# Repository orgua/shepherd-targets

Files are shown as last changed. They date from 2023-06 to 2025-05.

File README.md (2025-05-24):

# Target Boards & Firmware





**Main Documentation**: <https://nes-lab.github.io/shepherd>

**Source Code**: <https://github.com/nes-lab/shepherd-targets>

**Main Project**: <https://github.com/nes-lab/shepherd>

---

The repository contains a collection of target-hardware and mcu-firmwares used by the shepherd-testbed.
In the past shepherd had a nRF52-only target but can now leverage an additional FRAM, as demonstrated successfully by the
[Riotee-Platform](https://www.riotee.nessie-circuits.de).

**NOTE**: The shepherd testbed has a second target-port (unused) and is looking for ideas.
Just contact us if you got ideas.

## nRF52 with MSP430FR as FRAM

Hardware v1.3+ uses

- nRF52840
- MSP430FR5994 (TI)
- RTC AB1805

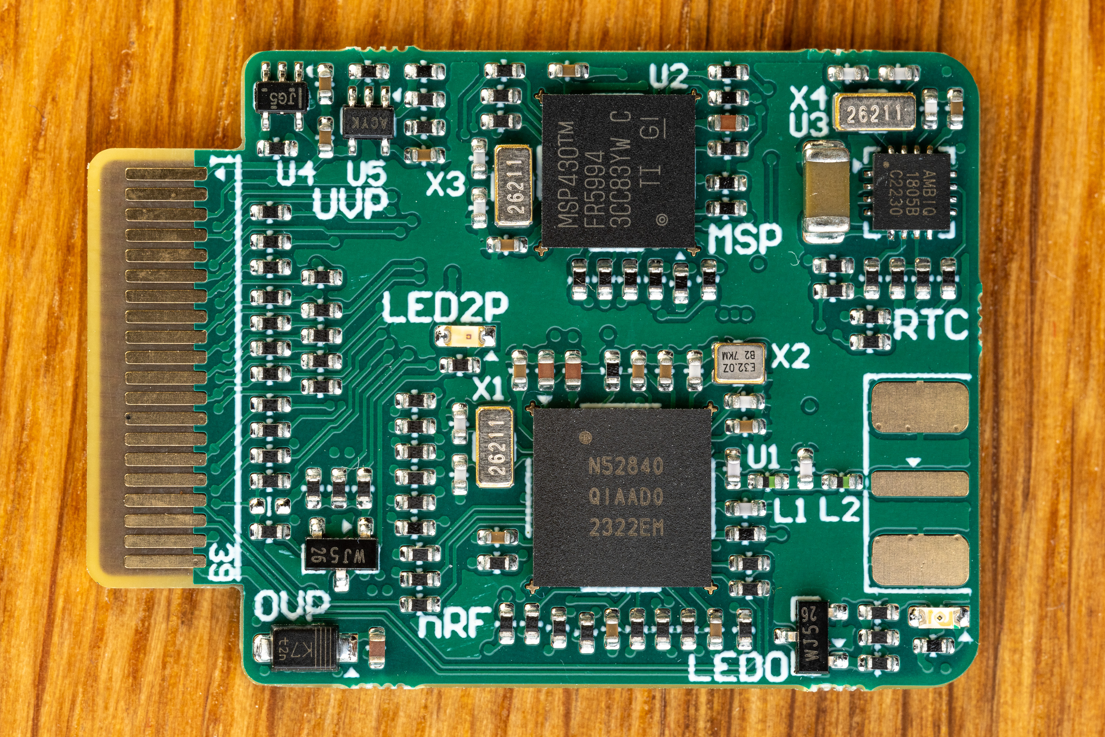
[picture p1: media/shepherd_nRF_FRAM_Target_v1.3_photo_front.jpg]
Target_nRF_MSP430


BOM, gerber-files and schematics are available in the [PCB-Directory](https://github.com/nes-lab/shepherd-targets/tree/main/hardware).
This folder also contains a guide for testing new target-PCBs.

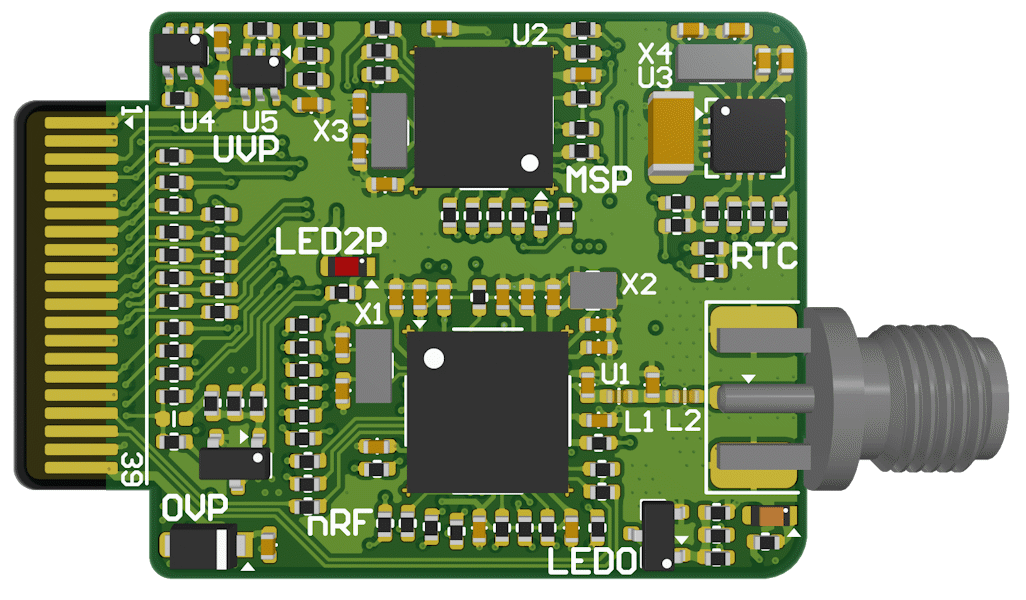
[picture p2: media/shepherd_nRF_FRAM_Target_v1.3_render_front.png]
Target_nRF_MSP430_render


### Features

- freedom to use both MCUs as needed (just as radio or FRAM) or disable when not needed (deep sleep)
- over-voltage protection for V_LV (max 3.9V)
- under-voltage protection with hysteresis for nRF
- one debug LEDs with separate supply for minimal impact on pwr-budget
- one self-powered LED to "burn" energy
- io pins not interfering with RF (nRF PS v1.6 page 578)
- LEDs / UART similar to [Riotee](https://www.riotee.nessie-circuits.de/)
- nRF uses low voltage mode (PSv1.1 page 61)
- 16x GPIO shared to host, current-limited with 240R star-configuration (every participant has that resistor on its port to also keep data rates >10 MHz)
- high & low power-good-signal (similar to riotee)
- SMA-port for external antenna
- 3rd possible way for reset (external), beside jtag and pwr-cycle

### nRF52-Firmwares

- [nrf52_demo_rf](https://github.com/nes-lab/shepherd-targets/tree/main/firmware/nrf52_demo_rf): demo implementation for a simple node that sends BLE packets when energy budget allows it
- [nrf52_testable](https://github.com/nes-lab/shepherd-targets/tree/main/firmware/nrf52_testable): watches all gpio and reports with UART messages (verification after assembly)
  - ensures that pcb is assembled OK and both MCUs are programmable and show basic functions
  - what is not tested: watchdog, FRAM, RF-Frontend (-> use rf-demo or rf-survey), sleep power consumption
- [nrf52_rf_test](https://github.com/nes-lab/shepherd-targets/tree/main/firmware/nrf52_rf_test): sends out 1 BLE-Packet per second (verify with an app like `RaMBLE`)
- [nrf52_rf_survey](https://github.com/nes-lab/shepherd-targets/tree/main/firmware/nrf52_rf_survey): Link Matrix Generator - TX-Unit - sends packet with every possible P_TX, loops until stopped
- [nrf52_deep_sleep](https://github.com/nes-lab/shepherd-targets/tree/main/firmware/nrf52_deep_sleep): practically turned off MCU with the lowest possible consumption

- TODO: nrf52_spi_radio - default implementation to use nRF as a radio frontend

### MSP430FR-Firmwares

- [msp430_deep_sleep](https://github.com/nes-lab/shepherd-targets/tree/main/firmware/msp430_deep_sleep): practically turned off MCU with the lowest possible consumption
- [msp430_spi_fram](https://github.com/nes-lab/shepherd-targets/tree/main/firmware/msp430_spi_fram): [riotee](https://github.com/NessieCircuits/Riotee_MSP430Fram) implementation to use MSP as a flash storage
- [msp430_testable](https://github.com/nes-lab/shepherd-targets/tree/main/firmware/msp430_testable): switches on all shared gpio one by one (verification after assembly)

## Getting started

Step by step description for installing all prerequisites to compile the firmware.

### nRF52

- Make sure you have the [GNU Arm Embedded Toolchain](https://developer.arm.com/tools-and-software/open-source-software/developer-tools/gnu-toolchain/gnu-rm/downloads) installed
- If `arm-none-eabi-gcc` is not in your path, set the environment variable `GNU_INSTALL_ROOT` accordingly, e.g.: `export GNU_INSTALL_ROOT=/opt/toolchain/` (note the trailing foreslash)
- Download the nRF5 SDK from [here.](https://www.nordicsemi.com/Software-and-tools/Software/nRF5-SDK/Download) (You don't need a SoftDevice) and extract it
- Set the environment variables `SDK_ROOT` to the corresponding absolute path, e.g.: `export SDK_ROOT=/home/user/nRF5_SDK_17.0.2_d674dde/`
- run `make`

Refer to [the GitHub workflow](https://github.com/nes-lab/shepherd-targets/tree/main/.github/workflows/build_nrf.yaml) for how to install the toolchain and build the project.

### MSP430

To build the code, you'll need the gcc toolchain for the MSP430 microcontroller series. Refer to [the GitHub workflow](https://github.com/nes-lab/shepherd-targets/tree/main/.github/workflows/build_msp.yaml) for how to install the toolchain and build the project.

### Controlling the Node-ID

When an `elf`-firmware contains a ``SHEPHERD_NODE_ID``, the variable will be patched with the actual target-ID before running the experiment. See the proposed [c-file](https://github.com/nes-lab/shepherd-targets/tree/main/firmware/nrf52_demo_rf/src/shepherd_node_id.c) for more information.

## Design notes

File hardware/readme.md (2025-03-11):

# PCBs and other hardware

This directory contains all files to manufacture hardware:

- schematic
- PCB-renderings (end of schematic pdfs)
- gerber for pcb manufacturing
- BOM to order parts
- pick and place and assembly drawings for PCB assembly

## nRF52 & MSP430 FRAM Target

- V1.0 was the initial target used by the testbed
- ~~V1.1 was designed, but is not yet manufactured~~
- ~~V1.2 was designed and tested - discarded because of manufacturing problems~~
- V1.3 is being deployed ATM
- V1.3e will accompany the base-version and will hopefully reduce failure-rate of msp430

## Adapters

- debug-board for target v1.3 that can sit between cape and target and breaks out all GPIO to 0.1" header
- converter for cape v2.4 header to target v1.3 edge-connector

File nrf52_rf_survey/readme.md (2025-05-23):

# nRF using TrafficBench to survey the rf-conditions for the testbed

Trafficbench is configured to let each node send a packet. The other nodes listen automatically and try to capture the packet and also record the P_Rx.

Current configuration

- loop - one node after the other talks - the others listen
- each node sends ~ 34 bytes via 1 MBit Bluetooth (~300 us airtime), PTx = 0 dBm
- the other nodes listen and capture for 5 ms (+ 500 us pre- & post-delay)
- sleep 1 s before next node begins

## Installation

- adapt schedule with the [schedule-builder-script](./schedule_builder/build.py)
- compiling: follow the [readme](./trafficbench/README.md) of trafficbench
  - newest studio version (tested with v7.30) is fine
  - extra package needed (and restart studio after install) - should be automatic: CMSIS 5 5 CMSIS-CORE Support Package

## Usage of ELF

- patch SHEPHERD_NODE_ID in elf-file for each node (see [example python script](./_build/update_and_patch.py))
- run on testbed
- postprocessing, TODO
- NOTE: first loop-cycle should be discarded

## Changes compared to vanilla trafficbench

- change testbed: flocklab -> shepherd
- correct spelling
- fix formatting
- fix for sensitivity to include-order: added #include "traffic_bench.h" in cbor.h
- removed node-id-magic in main.c (line 154:217)
- transformed py-scripts to be more accessible

specially for shepherd

- reduced uart-speed to 115_200 for now (in config.h)
- disable flow control (readme warns about it) to just stream uart (`mode=0` in config.h)
- disable button press to start (section removed in main.c)
- deactivate DEBUG_GPIO in `radio.c`
- current GPI modifications
  - reformatted with projects clang-format
  - use `GPI_ARCH_BOARD_TUDNES_SHEPHERD_NRF52840FRAM_V13` as `GPI_ARCH_PLATFORM` in `trafficbench/config.h`
  - added `#include "gpi/arm/nordic/nrf528xx/platform_internal.h"` in `trafficbench/target/nrf52840/radio_queues_custom.h` to add back macros for trafficbench
  - added `#define LED_SYNC GPI_LED_0` for our target `#elif GPI_ARCH_IS_BOARD(TUDNES_SHEPHERD_NRF52840FRAM_V13)` in `trafficbench/scheduler.c`

## Usage on the testbed

on server - prereq:

```shell
cd ~
git clone https://github.com/nes-lab/shepherd-tools
cd shepherd-tools/extr

python3 gen_energy_envs.py
python3 gen_firmwares.py
python3 gen_rf_survey.py
# current firmware is now in /var/shepherd/content/fw/, accessible by all observers
# task is also accessible for all observers, but in our case we send it out via herd-tool
```

for the actual run:
```Shell
shepherd-herd -v run -a /var/shepherd/content/task/nes_lab/tasks_rf_survey.yaml
# this takes ~ 8min and will exit after. Then we collect the data
scp
```

scp /var/shepherd/recordings/

## TODO:

- vary send-power (?)
- look for other IO used by TB
  - gpi_button_read() in main.c
  - gpi_led_toggle() in main.c
  - gpi_led_on() & gpi_led_off() in scheduler.c
  - LED_SYNC, GPI_LED_2
  - GPI_BUTTON_SIG1, GPI_BUTTON_1
- py:
  - filter_log.py and more
  - make code usable by other py-code
  - modularize + make testable
- speed up loop
  - 1 ms tx-delay
  - 3 ms tx-timeout
  - 15 - 50 ms sleep
  - factor in TRX_PRE_DELAY and _POST_DELAY
- packet-content: all random data might improve prx-consistency

## Source

https://gitlab.com/nes-lab/trafficbench

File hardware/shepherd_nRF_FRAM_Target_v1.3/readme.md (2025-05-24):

# nRF52 & MSP430 FRAM Target V1.3

Shared pins between MCUs and Observers with **Cape V2.5 (currently evaluated)**.
**The testbed still uses Cape v2.4 as of 2025-04. See 2nd table below for that mapping.**

| SHP-V26  | Dir   | Riotee     | nRF52  | msp430  | Description                 |
|----------|-------|------------|--------|---------|-----------------------------|
| GPIO0    | <-A-> | GPIO.0     | P0.21  | P2.6    | UART Target-RX, msp.A1.CiPo |
| GPIO1    | <--   | GPIO.1     | P0.08  | P2.5    | UART Target-TX, msp.A1.CoPi |
| GPIO2    | <-B-> | GPIO.2     | P0.04  | P2.3    | msp.A1.PSel                 |
| GPIO3    | <-B-> | GPIO.3     | P0.05  | P2.4    | msp.A1.CLK                  |
| GPIO4    | <-C-> | GPIO.4     | P1.09  | P4.6    |                             |
| GPIO5    | <-C-> | GPIO.5     | P0.26  | P3.6    |                             |
| GPIO6    | <-C-> | GPIO.6     | P1.03  | PJ.6    |                             |
| GPIO7    | <-C-> | GPIO.7     | P0.11  | P5.3    | msp.B1.PSel                 |
| GPIO8    | <--   | GPIO.8     | P0.13  | P5.2    | msp.B1.CLK                  |
| GPIO9    | <--   | GPIO.9     | P0.16  | P5.1    | msp.B1.CiPo                 |
| GPIO10   | <--   | -          | P0.12  | P5.0    | msp.B1.CoPi, SDA            |
| GPIO11   | <--   | -          | P0.10  | P6.0    | msp.A3.CoPi, TXD            |
| (GPIO12) | <--   | -          | P0.19  | P6.1    | msp.A3.CiPo, RXD            |
| (GPIO13) | <--   | -          | P0.20  | P6.3    | msp.A3.STE                  |
| (GPIO14) | <--   | -          | P0.24  | P6.6    | msp.A3.CLK                  |
| (GPIO15) | <--   | -          | P0.27  | P6.7    | msp.A3.STE                  |
| PwrGoodL | -->   | PG_L       | P0.23  | P5.4    |                             |
| PwrGoodH | -->   | PG_H       | P0.07  | P5.5    |                             |
| prog11   | -->   | SWD.CLK    | swdclk | -       |                             |
| prog12   | <-D-> | SWD.IO     | swdio  | -       |                             |
| prog21   | -->   | SBW.CLK    | -      | sbwtck  |                             |
| prog22   | <-E-> | SBW.IO     | -      | sbwtdio |                             |
|          | -     | LED.0      | P1.13  | P5.7    |                             |
|          | -     | LED.2P     | P0.03  | PJ.0    |                             |
|          | -     | I2C.SCL    | P1.08  | P6.5    |                             |
|          | -     | I2C.SDA    | P0.06  | P6.4    |                             |
|          | -     | RTC.INT    | P0.30  | P7.3    | shared, no fct for shp      |
|          | -     | MAX.INT    | P0.30  | PJ.1    | shared, no fct for shp      |
|          | -     | C2C.CLK    | P0.18  | P1.5    | msp.A0.CLK                  |
|          | -     | C2C.CoPi   | P0.17  | P2.0    | msp.A0.CoPi                 |
|          | -     | C2C.CiPo   | P0.14  | P2.1    | msp.A0.CiPo                 |
|          | -     | C2C.PSel   | P0.22  | P1.4    | msp.A0.PSel                 |
|          |       | C2C.GPIO   | P0.15  | PJ.2    |                             |
|          |       | THRCTRL.H0 | P0.09  | P1.3    | shared, no fct for shp      |
|          |       | THRCTRL.H1 | P1.02  | P3.3    | shared, no fct for shp      |
|          |       | THRCTRL.L0 | P1.07  | P6.2    | shared, no fct for shp      |
|          |       | THRCTRL.L1 | P1.04  | P7.0    | shared, no fct for shp      |
|          |       | VCAP.Sense | P0.29  | P7.5    | VTarget                     |

**Note**:

- A, B, C in DIR-Column refer to switch-groups. 1, 2 and/or 4 bits can be reversed to talk to the target.
- D, E are switch-groups needed for programming
- Shepherds GPIO12 to GPIO15 are not recordable by the testbed as pins on the SBC are all used up

## Connections to Cape V2.4 via Adapter

The 40-pin Edge-Connector of Target V1.3 has an adapter to interface the 2x9 Header of Cape V2.4. This keeps connections compatible to Target V1.0.

| SHP-V24 | Dir   | Riotee   | nRF52  | msp430  | Description                 |
|---------|-------|----------|--------|---------|-----------------------------|
| GPIO0   | <-A-> | GPIO.7   | P0.11  | P5.3    | msp.B1.PSel                 |
| GPIO1   | <-A-> | GPIO.8   | P0.13  | P5.2    | msp.B1.CLK                  |
| GPIO2   | <-A-> | GPIO.2   | P0.04  | P2.3    | msp.A1.PSel                 |
| GPIO3   | <-A-> | GPIO.3   | P0.05  | P2.4    | msp.A1.CLK                  |
| GPIO4   | <--   | GPIO.4   | P1.09  | P4.6    |                             |
| GPIO5   | <--   | GPIO.5   | P0.26  | P3.6    |                             |
| GPIO6   | <--   | GPIO.6   | P1.03  | PJ.6    |                             |
| GPIO7   | <--   | GPIO.1   | P0.08  | P2.5    | UART Target-TX, msp.A1.CoPi |
| GPIO8   | <-B-> | GPIO.0   | P0.21  | P2.6    | UART Target-RX, msp.A1.CiPo |
| BATOK   | -->   | PG_H     | P0.07  | P5.5    |                             |
| prog11  | -->   | SWD.CLK  | swdclk | -       |                             |
| prog12  | <-C-> | SWD.IO   | swdio  | -       |                             |
| prog21  | -->   | SBW.CLK  | -      | sbwtck  |                             |
| prog22  | <-D-> | SBW.IO   | -      | sbwtdio |                             |

**Note**:
- A, B, C, D in DIR-Column refer to switch-groups
- Shepherds GPIO8 (target-rx) will be re-assigned to PwrGoodL (BATOK is PwrGoodH)
  - TODO: Resistor-Switch on adapter available, but software not ready yet

## Features

- similarity to Riotee
- MCU 1 - nRF52840
- MCU 2 - msp430FR5994
- low power RTC & Watchdog
- one led to burn energy fast
- SMA port to connect external antenna
  - balun is optimized for higher transmit power (>= 5 dBm, ref circuit 7 in PS v1.8)
- MCUs share SPI-Connection + some additional pins
- edge-connector routes out
  - programming pins (SWD & SBW)
  - power-good signals
  - 16x shared GPIO
- all shared GPIO is current limited to prevent damages to the hardware
  - limit to 8-10 mA @ 4V with 470 R or (2x) 220 R on each IC entry
- IO-Pins not interfering with RF (nRF PS v1.6 page 578)
- clock-crystals have high precision, 5 ppm, with matched impedance
- protection for over- & under-voltage, see sub-chapters below

### Over-Voltage-Protection

The target voltage coming from the shepherd-cape can reach up to 5 V.
The MCUs on the target board can't handle that voltage, so the ICs have to be protected.

Abs Max Ratings:

- 3.9 V nRF52
- 3.8 V RTC AB1805
- 4.1 V MSP430

A fitting shottky diode is used to burn energy above 3.7V.

One PMEG10010ELR Diode is between V_target and 3V3:
+ 0.0 V -> 6 pA (noise)
+ 0.1 V -> 47 nA
+ 0.2 V -> 2.3 uA
+ 0.3 V -> 120 uA
+ 0.4 V -> 4.83 mA

### Under-Voltage-Protection

- the nRF consumes ~.5mA below 1.7V, even in deep-sleep
- consumption drops when going above 1.69 V
- consumption rises when going below 1.58 V
- tested 13 nodes range from
   - ON = 1.63 to 1.69 V
   - OFF = 1.58 to 1.60 V

Solution

- analog switch controlled by comparator with small hysteresis
- VON = 1.729 V, VOFF = 1.652 V according to formular in datasheet (values are wrong?)
- VON = 1.797 V, VOFF = 1.642 V when solving the network with traditional methods
- VON = 1.802 V, VOFF = 1.641 V from actual measurements

Possible Caveats

- hysteresis is currently only 150 mV and unstable behavior must be avoided
- charging the decoupling caps (2.6 uF) of the MCUs leads to voltage drop
  - 10 uF storage, 2.6 uF decoupling -> 230 mV drop (trouble)
  - 47 uF storage, 2.6 uF decoupling -> 48 mV drop
  - 100 uF storage, 2.6 uF decoupling -> 22 mV drop
- turning on the switch shows current spike of ~ 4 mA for < 50 us for target v1.0 with 1.6 uF decoupling
  - 10 uF storage, 5 mA draw -> 200 us for 100 mV drop
  - 10 uF storage, 1 mA draw -> 1000 us for 100 mV drop
  - 47 uF storage, 5 mA draw -> 940 us for 100 mV drop
  - 100 uF storage, 5 mA draw -> 2000 us for 100 mV drop

Calculating the charging drop for the decoupling caps with `maxima`:

```maxima
C_store: 10e-6;
C_out: 2.6e-6;
V_set: 1.7;
dVc: V_set * (sqrt(1 - C_out / C_store) - 1);
```

Calculating the allowed time for high current during switching on:

```maxima
V_set: 1.7;
C_store: 10e-6;
I_out: 5e-3;
dV: 100e-3;
t: dV * C_store / I_out;
```

See `.wxmx`-maxima-file for more details.

## Difference to Riotee

- nRF52840 instead of Riotees -833
  - main makefile specifies `NRF_DEV_NUM`
- msp430FR5994 has more storage (256 KB)
  - Size of FRAM auto-adjust? -> main makefile `RIOTEE_RAM_RETAINED_SIZE`, `RIOTEE_STACK_SIZE`
- extra LED.0
- 16x GPIO instead of 10x
- no power-converters, but over-voltage-protection and under-volt-switch for nRF

## Bugs of prior Version & Proposed Fixes / Improvements

- nRF - remove resist of alignment crosses
- less paste on thermal pad of nRF? Thermal paste is OK
  - solder on thermal is 9 * 1.1² = 8.6 mm² (round) -> 38 %
  - info: nRF-IC thermal pad ~4.75², 22.6 m² (IC and footprint match)
- make ABx Thermal pad bigger
  - info: ABx-IC thermal pad is ~ (1.8 mm)²
  - datasheet says D2xE2 is 1.65 - 1.75 - 1.85 -> area: 2.6 - 3.1 - 3.4 mm²
  - footprint was (1.13mm)² with 50% paste reduction (1.27 / 0.65 mm²)
  - now it is 1.5² with 65% reduction (2.25 / 0.79 mm²)
- stencil holes of nRF a bit bigger - pad 0.26mm round = 53.1e-3 mm², now with .28mm stencil (.213 distance, 61.6e-3 mm²)
  - ref design: pads .275mm with 19% expansion (.012mm) -> measured .299 (area .0594, .0647, .0702 for .275, .287, .299)
- stencil holes of MSP a bit bigger - pad 0.25mm round = 49.1e-3 mm², now with .28mm stencil (.213 distance)
- 1uF has two versions in BOM -> 10V version stays
- make more clear what is DNP -> Variants "Only Populate" changes Value, Mnf PN, Price to DNP
- Riotee has an MSP430FR5962 (like target v1.0) and not the current 5994?!? (256 vs 128 kByte)
  - linker and makefile needed a small adaption (include proper device-file)
  - Riotees FRAM-firmware is adapting automatically to FRAM-Size
  - datasheets memory map (section 9.15) shows identical maps with just double the FRAM-Space (end at x43FFF instead of x23FFF)
- why did the crystals footprint change (larger) but not the part? tombstone rate ~ 50%
  - correct crystal for that larger footprint: 520-ECX-.327CDX-1293, 5ppm, 3.2x1.5mm -> all correct & available
  - OLD: CM8V-T1A-32.768kHz-9pF-20PPM-TA-QC, 20ppm, 2.0x1.2mm
- add C on ABx-Crystal? YES - datasheet is misleading by not showing any
- board dimensions:
  - capes 54.8 / 2 = 27.4 mm max width -> 27
  - edge-connector, slit-bit is 6 x 17.4 mm -> side cutout is 6 x 4.8
  - target with hdr is 38.2 mm, so limiting the whole length now to 37
  - old-area was 25 x 24 = 600 mm², new usable area is 27 x 31 = 837
- nRF has high current draw between 500...1650 mV -> VSrc with diode+cap is problematic
  - voltage sweep is plotted in [this graphic](emu_ramp.plot_0s000_to_40s000.png) and other
  - add comparator to delay power of nRF
  - fix targets: comparator + pwr-switch -> on when above 1.65 .. 1.70 V
    - off again when going below 1.4 V
  - 2x 6.5 MOhm Divider to
  - ~~TS5A23166DCUR~~ -> needs comparator
  - ~~in our stock: NLAS4684, FSA2258~~
  - 595-TS5A3167DCKR, ROn .9 Ohm, SC70-5, 50nA supply, SPST -> V_analog_max = VCC, V_EN_max = VIn_max = 6.5V
    - COM connected to NC (normally closed) when logic is LOW, so input is nEN!
  - 579-MCP6546RT-IOT, comparator, VIN+ gets Ref ResistorNW, When VIN- is below VIN+ the output is high (WANTED)
    - open drain output, so PU to 3V3 - switch has <20nA leakage, so ~100k should be fine
- extend to 16 GPIO
  - order adapter to old shepherd 2x9
  - order pinheader and sockets for the new port
  - which pins to add?
  - 2x10 Angled Socket: SQT-110-01-F-D-RA -> new 2x13: SQT-113-01-F-D-RA -> without Angle: SQT-113-01-F-D
  - 2x10 PinHeader: 2PH2-20-UA -> new 2x13 only available from samtec, but they fit next to each other -> 2PH2-16-UA + 2PH2-10-UA
  - width: 20.35/10*13=26.5mm or better 20.35/11*14=25.9mm, MAX of Cape is 54.7/2=27.35mm
  - PCB-Edge-Connectors: https://www.mouser.de/c/connectors/card-edge-connectors/?number%20of%20positions=26%20Position%7C~30%20Position&instock=y&active=y&sort=pricing
    - PCIe 1x is cheap, has 1 mm distance and comes as TH & SMD, but it is designed for thick PCBs
    - HSEC8-120-01-S-DV-A-GR-K: 40Con, Guide Rails 7x20.6mm 11.75mm high
    - HSEC8-120-01-S-DV-A-K: without guide rails only 7.8mm high
    - **HSEC8-120-01-L-DV-A-K-TR**: same, but cheaper
  - ~~FFC/FPC-Con~~: https://www.mouser.de/c/connectors/ffc-fpc/ffc-fpc-connectors/?number%20of%20positions=26%20Position%7C~28%20Position%7C~30%20Position%7C~32%20Position&instock=y&active=y
  - ~~FFC/FPC-Cable~~: https://www.mouser.de/c/connectors/ffc-fpc/ffc-fpc-jumper-cables/?number%20of%20conductors=26%20Conductor%7C~28%20Conductor%7C~30%20Conductor%7C~32%20Conductor&instock=y&active=y
- current-limit LED0 (MSP430 is lower prio, so it gets 470R)
- **NEW GPIO**
  - GP10 P0.12  P5.0 (UCB1SIMO/SDA)
  - GP11 P0.10  P6.0 (UCA3SIMO/TXD)
  - GP12 P0.19  P6.1 (UCA3SOMI/RXD)
  - GP13 P0.20  P6.3 (UCA3STE)
  - GP14 P0.24  P6.6 (UCA3CLK)
  - GP15 P0.27  P6.7 (UCA3STE)
  - LED0 P1.13  P5.7
- verify RF-Path
  - PS_v1.8 ref circuit 7 shows improved 4 component filter: 1pF, 4.7nH, 1.2pF, 2.2nH (NP0 5%, hf ind. 5%)
  - keepout under antenna-path for
  - fanout shorter and thinner, C1 directly on RFOUT and GND
- review problematic pins
- also disable MSP with switch (avoids cross-feeding via gpio)

## Cost of Production

- PCB-Fabrication
  - 190 € / 30 n with shipping
  - 1.6mm thick, 4 layer, .3mm vias - filled and capped, .1 mm traces and distance
  - electro-polished stencil
- BOM cost
  - parts for 1 n when ordering 10 n = 20.60 €
  - parts for n=10 are 182 € (18.20 €/n)
  - parts for n=20 are 360 € (18 €/n)
- Pick & place
  - 29 different parts, 120 in total
  - 0.5 mm pitch

### Ordering of Parts

- new C27 1pF: 100x 81-GJM1555C1H1R0JB1D
- new C28 1.2pF: 100x 81-GJM1555C1H1R2JB1D
- new L2 2.2nH: 100x 81-LQG15HZ2N2C02D
- ~~SMA-Con?~~
- new HSEC8-120-01-L-DV-A-K-TR: 20x 200-HSEC812001LDVAKT
  - new headers for old cape?
- more 1uF - 4x30 - 200x 81-GCM155C71A105KE8D
- more 12pF -8x30 - 250x 77-VJ0402A120JXQPBC
- 12x 240R per unit (more IO)
- switch + comparator (MCP6546, TS5A3167)
  - 3x 100k, 1x 10k, 1x 1M,
  - 2x 100nF
- 1x 470R

### Extra remark

- DNP: C20, SMA-Con, Antenna

## Verifying the PCBs

- first do a visual inspection
- front side has one cap DNP: C20, lower left corner, near edge-connector

### Assembly

- solder the SMA-Connector, add Antenna

### First Powerup

- 2 mA @ 3V on V_target without programming
- 0 mA @ 3V on 3V-Input

### Software-Prereqs

**NOTE**: all further tests are done on BBone

```Shell
cd ~
git clone https://github.com/nes-lab/shepherd-tools
cd shepherd-tools
git checkout dev
git pull

python3 ./extra/gen_firmwares.py
sudo python3 ./extra/gen_experiments.py
```

Put Target on BBone with Target on Port 1!

### Test all GPIO & LEDs

First test all used gpio with this fw-combo (msp toggles, nrf watches and reports via uart):

```Shell
sudo shepherd-sheep program -p A -m 1 -v 3 -t nrf52 /var/shepherd/content/fw/nes_lab/nrf52_testable/build.hex
sudo shepherd-sheep program -p A -m 2 -v 3 -t msp430 /var/shepherd/content/fw/nes_lab/msp430_testable/build.hex
sudo shepherd-sheep target-power -p A -v 3 --on
# new
sudo shepherd-sheep run /etc/shepherd/target_device_test1.yaml
```

NOTE: best done with inter-connector that only routes: pwr1, serial, programming-pins, pwr2
Check UART output with logic analyzer or in shepherd recording.
Behavior is described [here](https://github.com/nes-lab/shepherd-targets/tree/main/firmware/nrf52_testable).

### Testing the Radio

```Shell
sudo shepherd-sheep program -p A -m 1 -v 3 -t nrf52 /var/shepherd/content/fw/nes_lab/nrf52_rf_test/build.hex
sudo shepherd-sheep program -p A -m 2 -v 3 -t msp430 /var/shepherd/content/fw/nes_lab/msp430_deep_sleep/build.hex
sudo shepherd-sheep target-power -p A -v 3 --on
# new
sudo shepherd-sheep run /etc/shepherd/target_device_test2.yaml
```

Behavior is described [here](https://github.com/nes-lab/shepherd-targets/tree/main/firmware/nrf52_rf_test).

### Testing Power-consumption during sleep

```Shell
sudo shepherd-sheep program -p A -m 1 -v 3 -t nrf52 /var/shepherd/content/fw/nes_lab/nrf52_deep_sleep/build.hex
sudo shepherd-sheep program -p A -m 2 -v 3 -t msp430 /var/shepherd/content/fw/nes_lab/msp430_deep_sleep/build.hex
# new
sudo shepherd-sheep run /etc/shepherd/target_device_test3.yaml
```

## Testing

- programming via debug-adapter fails for nRF (OK for MSP), even at 200kbit or 100kbit instead of 500k
  - reason: unsoldered press-fit to shepherd cape
- 6 of 24 targets had trouble programming the MSP
  - removing two ICs showed no flaws
  - as visual inspection is OK the next suspects are: pcb or chip-failure
- report is in [planning-repo](https://github.com/orgua/shepherd-v2-planning/tree/main/doc_testbed)

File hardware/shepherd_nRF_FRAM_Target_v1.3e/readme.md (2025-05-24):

# nRF52 & MSP430 FRAM Target V1.3e

Shared pins between MCUs and Observers with **Cape V2.5 (deployed in near future / mid 2025)**.

**The testbed still uses Cape v2.4 as of 2025-04. See 2nd table below for that mapping.**

**Note**:

- GPIO12 to GPIO15 are not recordable by the testbed with cape V2.5, as pins on the SBC are all used up
- The nRF has no outer reset line - so configuring one could keep the MCU in permanent reset. Code for the nRF52-DK may use P0.21 for reset - it is actively used for UART-Rx here.
- A, B, C in DIR-Column refer to switch-groups. 1, 2 and/or 4 bits can be reversed to talk to the target.
- D, E are switch-groups needed for programming

| Tgt-Port | Dir   | Riotee     | nRF52  | msp430  | Description                 |
|----------|-------|------------|--------|---------|-----------------------------|
| GPIO0    | <-A-> | GPIO.0     | P0.21  | P2.6    | UART Target-RX, msp.A1.CiPo |
| GPIO1    | <--   | GPIO.1     | P0.08  | P2.5    | UART Target-TX, msp.A1.CoPi |
| GPIO2    | <-B-> | GPIO.2     | P0.04  | P2.3    | msp.A1.PSel                 |
| GPIO3    | <-B-> | GPIO.3     | P0.05  | P2.4    | msp.A1.CLK                  |
| GPIO4    | <-C-> | GPIO.4     | P1.09  | P4.6    |                             |
| GPIO5    | <-C-> | GPIO.5     | P0.26  | P3.6    |                             |
| GPIO6    | <-C-> | GPIO.6     | P1.03  | PJ.6    |                             |
| GPIO7    | <-C-> | GPIO.7     | P0.11  | P5.3    | msp.B1.PSel                 |
| GPIO8    | <--   | GPIO.8     | P0.13  | P5.2    | msp.B1.CLK                  |
| GPIO9    | <--   | GPIO.9     | P0.16  | P5.1    | msp.B1.CiPo                 |
| GPIO10   | <--   | -          | P0.12  | P5.0    | msp.B1.CoPi, SDA            |
| GPIO11   | <--   | -          | P0.10  | P6.0    | msp.A3.CoPi, TXD            |
| (GPIO12) | <--   | -          | P0.19  | P6.1    | msp.A3.CiPo, RXD            |
| (GPIO13) | <--   | -          | P0.20  | P6.3    | msp.A3.STE                  |
| (GPIO14) | <--   | -          | P0.24  | P6.6    | msp.A3.CLK                  |
| (GPIO15) | <--   | -          | P0.27  | P6.7    | msp.A3.STE                  |
| PwrGoodL | -->   | PG_L       | P0.23  | P5.4    |                             |
| PwrGoodH | -->   | PG_H       | P0.07  | P5.5    |                             |
| prog11   | -->   | SWD.CLK    | swdclk | -       |                             |
| prog12   | <-D-> | SWD.IO     | swdio  | -       |                             |
| prog21   | -->   | SBW.CLK    | -      | sbwtck  |                             |
| prog22   | <-E-> | SBW.IO     | -      | sbwtdio |                             |
|          | -     | LED.0      | P1.13  | P5.7    |                             |
|          | -     | LED.2P     | P0.03  | PJ.0    |                             |
|          | -     | I2C.SCL    | P1.08  | P6.5    |                             |
|          | -     | I2C.SDA    | P0.06  | P6.4    |                             |
|          | -     | RTC.INT    | P0.30  | P7.3    | shared, no fct for shp      |
|          | -     | MAX.INT    | P0.30  | PJ.1    | shared, no fct for shp      |
|          | -     | C2C.CLK    | P0.18  | P1.5    | msp.A0.CLK                  |
|          | -     | C2C.CoPi   | P0.17  | P2.0    | msp.A0.CoPi                 |
|          | -     | C2C.CiPo   | P0.14  | P2.1    | msp.A0.CiPo                 |
|          | -     | C2C.PSel   | P0.22  | P1.4    | msp.A0.PSel                 |
|          |       | C2C.GPIO   | P0.15  | PJ.2    |                             |
|          |       | THRCTRL.H0 | P0.09  | P1.3    | shared, no fct for shp      |
|          |       | THRCTRL.H1 | P1.02  | P3.3    | shared, no fct for shp      |
|          |       | THRCTRL.L0 | P1.07  | P6.2    | shared, no fct for shp      |
|          |       | THRCTRL.L1 | P1.04  | P7.0    | shared, no fct for shp      |
|          |       | VCAP.Sense | P0.29  | P7.5    | VTarget                     |

## Connections to Cape V2.4 via Adapter

The 40-pin Edge-Connector of Target V1.3 has an adapter to interface the 2x9 Header of Cape V2.4.
This keeps connections compatible to Target V1.0.

**Note**:
- A, B, C, D in DIR-Column refer to switch-groups
- Shepherds GPIO8 (target-rx) will be re-assigned to PwrGoodL (BATOK is PwrGoodH)

| SHP-V24 | Dir   | Riotee   | nRF52  | msp430  | Description                 |
|---------|-------|----------|--------|---------|-----------------------------|
| GPIO0   | <-A-> | GPIO.7   | P0.11  | P5.3    | msp.B1.PSel                 |
| GPIO1   | <-A-> | GPIO.8   | P0.13  | P5.2    | msp.B1.CLK                  |
| GPIO2   | <-A-> | GPIO.2   | P0.04  | P2.3    | msp.A1.PSel                 |
| GPIO3   | <-A-> | GPIO.3   | P0.05  | P2.4    | msp.A1.CLK                  |
| GPIO4   | <--   | GPIO.4   | P1.09  | P4.6    |                             |
| GPIO5   | <--   | GPIO.5   | P0.26  | P3.6    |                             |
| GPIO6   | <--   | GPIO.6   | P1.03  | PJ.6    |                             |
| GPIO7   | <--   | GPIO.1   | P0.08  | P2.5    | UART Target-TX, msp.A1.CoPi |
| GPIO8   | <-B-> | GPIO.0   | P0.21  | P2.6    | UART Target-RX, msp.A1.CiPo |
| BATOK   | -->   | PG_H     | P0.07  | P5.5    |                             |
| prog11  | -->   | SWD.CLK  | swdclk | -       |                             |
| prog12  | <-C-> | SWD.IO   | swdio  | -       |                             |
| prog21  | -->   | SBW.CLK  | -      | sbwtck  |                             |
| prog22  | <-D-> | SBW.IO   | -      | sbwtdio |                             |

## Features

- similarity to Riotee
- MCU 1 - nRF52840
- MCU 2 - msp430FR5994
- low power RTC & Watchdog
- one led to burn energy fast
- SMA port to connect external antenna
  - balun is optimized for higher transmit power (>= 5 dBm, ref circuit 7 in PS v1.8)
- MCUs share SPI-Connection + some additional pins
- edge-connector routes out
  - programming pins (SWD & SBW)
  - power-good signals
  - 16x shared GPIO
- all shared GPIO is current limited to prevent damages to the hardware
  - limit to 8-10 mA @ 4V with 470 R or (2x) 220 R on each IC entry
- IO-Pins not interfering with RF (nRF PS v1.6 page 578)
- clock-crystals have high precision, 5 ppm, with matched impedance
- protection for over- & under-voltage, see sub-sections below

### Over-Voltage-Protection

The target voltage coming from the shepherd-cape can reach up to 5 V.
The MCUs on the target board can't handle that voltage, so the ICs have to be protected.

Abs Max Ratings:

- 3.9 V nRF52
- 3.8 V RTC AB1805
- 4.1 V MSP430

A fitting shottky diode is used to burn energy above 3.7V.

One PMEG10010ELR Diode is between V_target and 3V3:
+ 0.0 V -> 6 pA (noise)
+ 0.1 V -> 47 nA
+ 0.2 V -> 2.3 uA
+ 0.3 V -> 120 uA
+ 0.4 V -> 4.83 mA

### Under-Voltage-Protection

- the nRF consumes ~.5mA below 1.7V, even in deep-sleep
- consumption drops when going above 1.69 V
- consumption rises when going below 1.58 V
- tested 13 nodes range from
  - ON = 1.63 to 1.69 V
  - OFF = 1.58 to 1.60 V

Solution

- analog switch controlled by comparator with small hysteresis
- VON = 1.729 V, VOFF = 1.652 V according to formular in datasheet (values are wrong?)
- VON = 1.797 V, VOFF = 1.642 V when solving the network with traditional methods
- VON = 1.802 V, VOFF = 1.641 V from actual measurements

Possible Caveats

- hysteresis is currently only 150 mV and unstable behavior must be avoided
- charging the decoupling caps (2.6 uF) of the MCUs leads to voltage drop
  - 10 uF storage, 2.6 uF decoupling -> 230 mV drop (trouble)
  - 47 uF storage, 2.6 uF decoupling -> 48 mV drop
  - 100 uF storage, 2.6 uF decoupling -> 22 mV drop
- turning on the switch shows current spike of ~ 4 mA for < 50 us for target v1.0 with 1.6 uF decoupling
  - 10 uF storage, 5 mA draw -> 200 us for 100 mV drop
  - 10 uF storage, 1 mA draw -> 1000 us for 100 mV drop
  - 47 uF storage, 5 mA draw -> 940 us for 100 mV drop
  - 100 uF storage, 5 mA draw -> 2000 us for 100 mV drop

Calculating the charging drop for the decoupling caps with `maxima`:

```maxima
C_store: 10e-6;
C_out: 2.6e-6;
V_set: 1.7;
dVc: V_set * (sqrt(1 - C_out / C_store) - 1);
```

Calculating the allowed time for high current during switching on:

```maxima
V_set: 1.7;
C_store: 10e-6;
I_out: 5e-3;
dV: 100e-3;
t: dV * C_store / I_out;
```

See `.wxmx`-maxima-file for more details.

## Difference to Riotee

- nRF52840 instead of Riotees -833
  - main makefile specifies `NRF_DEV_NUM`
- msp430FR5994 has more storage (256 KB)
  - Size of FRAM auto-adjust? -> main makefile `RIOTEE_RAM_RETAINED_SIZE`, `RIOTEE_STACK_SIZE`
- extra LED.0
- 16x GPIO instead of 10x
- no power-converters, but over-voltage-protection and under-volt-switch for nRF

## Cost of Production

- PCB-Fabrication
  - 190 € / 30 n with shipping
  - 1.6mm thick, 4 layer, .3mm vias - filled and capped, .1 mm traces and distance
  - electro-polished stencil
- BOM cost
  - parts for 1 n when ordering 10 n = 20.60 €
  - parts for n=10 are 182 € (18.20 €/n)
  - parts for n=20 are 360 € (18 €/n)
- Pick & place
  - 29 different parts, 120 in total
  - 0.5 mm pitch

### Extra remark

- DNP: C20, SMA-Con, Antenna

## Verifying the PCBs

- first do a visual inspection
- front side has one cap DNP: C20, lower left corner, near edge-connector

### Assembly

- solder the SMA-Connector, add Antenna

### First Powerup

- 2 mA @ 3V on V_target without programming
- 0 mA @ 3V on 3V-Input

### Software-Prereqs

**NOTE**: all further tests are done on BBone

```Shell
cd ~
git clone https://github.com/nes-lab/shepherd-tools
cd shepherd-tools
git checkout dev
git pull

python3 ./extra/gen_firmwares.py
sudo python3 ./extra/gen_experiments.py
```

Put Target on BBone with Target on Port 1!

### Test all GPIO & LEDs

First test all used gpio with this fw-combo (msp toggles, nrf watches and reports via uart):

```Shell
sudo shepherd-sheep program -p A -m 1 -v 3 -t nrf52 /var/shepherd/content/fw/nes_lab/nrf52_testable/build.hex
sudo shepherd-sheep program -p A -m 2 -v 3 -t msp430 /var/shepherd/content/fw/nes_lab/msp430_testable/build.hex
sudo shepherd-sheep target-power -p A -v 3 --on
# new
sudo shepherd-sheep run /etc/shepherd/target_device_test1.yaml
```

NOTE: best done with inter-connector that only routes: pwr1, serial, programming-pins, pwr2
Check UART output with logic analyzer or in shepherd recording.
Behavior is described [here](https://github.com/nes-lab/shepherd-targets/tree/main/firmware/nrf52_testable).

### Testing the Radio

```Shell
sudo shepherd-sheep program -p A -m 1 -v 3 -t nrf52 /var/shepherd/content/fw/nes_lab/nrf52_rf_test/build.hex
sudo shepherd-sheep program -p A -m 2 -v 3 -t msp430 /var/shepherd/content/fw/nes_lab/msp430_deep_sleep/build.hex
sudo shepherd-sheep target-power -p A -v 3 --on
# new
sudo shepherd-sheep run /etc/shepherd/target_device_test2.yaml
```

Behavior is described [here](https://github.com/nes-lab/shepherd-targets/tree/main/firmware/nrf52_rf_test).

### Testing Power-consumption during sleep

```Shell
sudo shepherd-sheep program -p A -m 1 -v 3 -t nrf52 /var/shepherd/content/fw/nes_lab/nrf52_deep_sleep/build.hex
sudo shepherd-sheep program -p A -m 2 -v 3 -t msp430 /var/shepherd/content/fw/nes_lab/msp430_deep_sleep/build.hex
# new
sudo shepherd-sheep run /etc/shepherd/target_device_test3.yaml
```

## Testing

- programming via debug-adapter fails for nRF (OK for MSP), even at 200kbit or 100kbit instead of 500k
  - reason: unsoldered press-fit to shepherd cape
- 6 of 24 targets had trouble programming the MSP
  - removing two ICs showed no flaws
  - as visual inspection is OK the next suspects are: pcb or chip-failure
- report is in [planning-repo](https://github.com/orgua/shepherd-v2-planning/tree/main/doc_testbed)

## Implemented Changes / Bugs of prior Version

- Edge-Connector is 17.40 mm wide, PCB-Edge has 17.20 mm, exactly to spec
  - resist bridge between pads is 0.3 mm, so this is fine, but pcb can be moved
  - -> still widen edge on both sides .05 mm to 17.30 mm (measures as 17.25 mm on final PCB)
  - connector wiggles and prongs are almost on outer edge of pad
- edge-connector is still a bit loose,
  - PCB has only 1.48 mm thickness without copper, resist, silk, but outer rail of connector is 1.75 mm (spec)
  - 1.64 to 1.70 mm on Cu, silk, resist -> measures as 1.64
  - railing edge now has resist and silk screen
- as 6 of 24 MSP430s were failing to be programmed - programming pins were checked & redone
  - R61 is 47k, but measures 4.0k? on failing boards R<3.9k, on good ones larger, more like 4.1
  - optimize via-placement with regard to distance from pad
- update parts from Libs
- panel - move holes of bridges a bit further out
- finished as v1.3e

**Production of v1.3e**

- BOM for 30n with spare, 650 € @ Mouser
- Panels for 30n, 214 € @ JLCPCB

## Errata & future Improvements

- BGA without paste? MSP-failure-rate stays ~ 20 %
  - low temp paste is harder to control - does not wet as good and needs manual fixes (almost on every PCB)
- bridge to panel should be moved away from BGA
- holes on panel can be 3.2 mm for stencil printer
- QR Code can now be directly created in Altium
- perforated breaking lines on panels (extension of milled line)
- bridge to panel can be thinner
- move LED a bit away from SMA
- pin 1 marking bigger on ICs
- is there a paste-pad under the TS5A?
- allow using internal switching regulator from nRF to lower power-consumption

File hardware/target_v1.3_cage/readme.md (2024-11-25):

## Cage for Target

This is a printable cage that protect the sensitive electronics.
Biofilm could add a resistive layer on the PCB that increases power-consumption of the target.

Printing was tested top-down with PLA. Support for the overhang can be added, but it also worked fine without it.

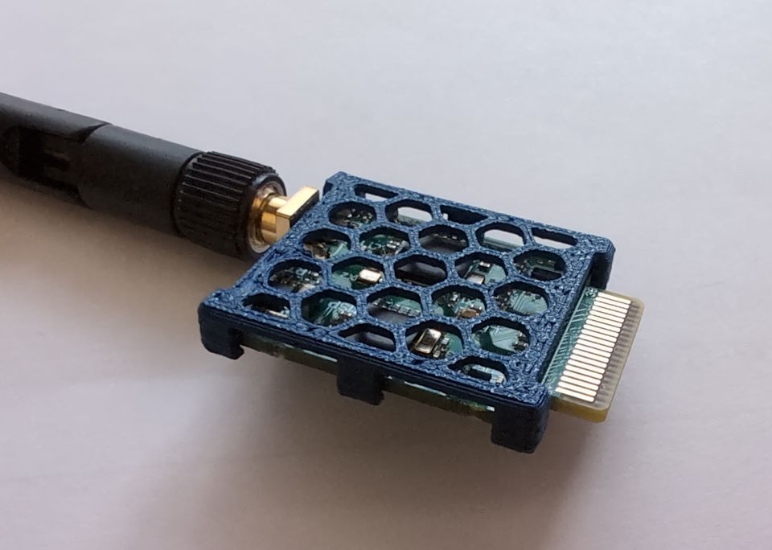
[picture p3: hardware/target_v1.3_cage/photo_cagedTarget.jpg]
cagedTarget


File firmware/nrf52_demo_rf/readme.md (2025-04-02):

# nrf52 demo for harvesting and rf

This firmware represents a typical intermittent application on a battery-free sensor node.
The app monitors the supply voltage and a GPIO pin.
If the supply voltage reaches 3.3V or the pin goes high, it sends a BLE advertisement packet and switches on an LED until the supply voltage drops below 3.3V or the pin goes low. The supply voltage is sampled with a frequency of 100Hz. The total current consumption in this mode is 5.6uA.

Edit the definitions of the GPIO pins at the top of `src/app.c` to reflect your hardware.

An App like `LightBlue` or `RaMBLE` can be used to monitor rf-activity.

## Source

https://github.com/geissdoerfer/shepherd-nrf52-demo

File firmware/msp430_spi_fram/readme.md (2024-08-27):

# MSP430 as SPI-FRAM (non-volatile memory)

The code in this repository turns an MSP430FR59XX microcontrollers into a general purpose non-volatile memory controlled via SPI.

The MSP430FR59XX series of microcontrollers come with on-board ferroelectric RAM (FRAM). In contrast to SRAM, this memory is non-volatile, i.e. it keeps its state without requiring periodic refreshes and without requiring a power supply. In contrast to flash memory, which must be erased before being written, FRAM can be treated just like SRAM and writing consumes very little energy.

NOTE: Makefile & linker are currently configured for the MSP430FR5994 (256 KB FRAM) instead of Riotees original FR5962 (128 KB)

## Interface

The firmware in this repository exposes a 4-wire SPI interface that allows reading and writing data to the on-board FRAM.
The SPI interface uses mode 0 (Clock low when inactive, data sampled on leading edge) and supports a frequency of 8MHz.

After the SPI controller pulls the CS line low, the peripheral (this firmware) sets up an initial transfer of 3 control bytes.
These three control bytes contain the 20-bit target address of the memory access and the type of operation (R/W).
The address is transferred lowest byte first.
If the highest bit of the third address byte is set, the operation is a write operation, otherwise it is a read operation.
After receiving the three command bytes, the peripheral will set up the corresponding DMA transfer and wait in a low power mode until the CS line goes high.
The controller shall keep the CS line low until the transfer has finished.
Upon this rising edge, the peripheral stops the transfer and transitions to low power mode again.

Transfers can have a maximum size of 65535 bytes.

## Timing requirements

The time from the falling edge of the CS line until the transmission of the first command byte must be at least 15us.
The time from the transmission of the last command byte to the transmission of the first data byte must be at least 25us.
The time from the rising edge of the CS line until the next falling edge of the CS line must be at least 10us.

## Memory map

The MSP430FR5962 has a total of 128kB FRAM.
Unfortunately, the interrupt vector table lives in the middle of this memory so the 128kB cannot be used contiguously. Instead, they are separated into two regions.
The lower region starts at 0x4000 and ends at 0xFF80 where the IVT lives.
The upper region starts at 0xFFFF and ends at 0x24000.
The code/data for this firmware also has to be placed within this area.
The linker script in this repository defines a dedicated section for the code and data of the firmware ranging from 0x4000 to 0x6000.

The remaining memory area from 0x6000 to 0x24000, excluding the IVT (0xFF80-0xFFFF) is available as data storage.
For an external application talking to the device over SPI, this memory gets mapped to 0x0000 to 0x1E000.
The firmware will protect the IVT from access.
Any operation extending over the IVT region or the end of the memory will get truncated without the controller noticing.

**The code on the SPI controller talking to this firmware must avoid reading/writing to the IVT region, which lies between 0x9F80 and 0x9FFF from its view.**

## Source

https://github.com/NessieCircuits/Riotee_MSP430Fram

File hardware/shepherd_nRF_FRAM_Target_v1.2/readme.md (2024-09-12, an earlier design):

# nRF52 & MSP430 FRAM Target V1.2

Shared pins between MCUs and Observer, **Cape V2.5 (not produced yet)**

| SHP-HDR  | Dir   | Riotee   | nRF52  | msp430  | Description                 |
|----------|-------|----------|--------|---------|-----------------------------|
| GPIO0    | <-A-> | GPIO.0   | P0.21  | P2.6    | UART Target-RX, msp.A1.CiPo |
| GPIO1    | <-B-> | GPIO.1   | P0.08  | P2.5    | UART Target-TX, msp.A1.CoPi |
| GPIO2    | <-C-> | GPIO.2   | P0.04  | P2.3    | msp.A1.PSel                 |
| GPIO3    | <-C-> | GPIO.3   | P0.05  | P2.4    | msp.A1.CLK                  |
| GPIO4    | <-C-> | GPIO.4   | P1.09  | P4.6    |                             |
| GPIO5    | <-C-> | GPIO.5   | P0.26  | P3.6    |                             |
| GPIO6    | <--   | GPIO.6   | P1.03  | PJ.6    |                             |
| GPIO7    | -->   | GPIO.7   | P0.11  | P5.3    | msp.B1.PSel                 |
| GPIO8    | <--   | GPIO.8   | P0.13  | P5.2    | msp.B1.CLK                  |
| GPIO9    | -->   | GPIO.9   | P0.16  | P5.1    | msp.B1.CiPo                 |
| PwrGoodL | -->   | PG_L     | P0.23  | P5.4    |                             |
| PwrGoodH | -->   | PG_H     | P0.07  | P5.5    |                             |
| prog11   | -->   | SWD.CLK  | swdclk | -       |                             |
| prog12   | <-A-> | SWD.IO   | swdio  | -       |                             |
| prog21   | -->   | SBW.CLK  | -      | sbwtck  |                             |
| prog22   | <-B-> | SBW.IO   | -      | sbwtdio |                             |
|          | -     | LED.0    | P0.12  | P5.0    | Riotee GPIO.10, msp.B1.CoPi |
|          | -     | LED.2P   | P0.03  | PJ.0    |                             |
|          | -     | I2C.SCL  | P1.08  | P6.5    |                             |
|          | -     | I2C.SDA  | P0.06  | P6.4    |                             |
|          | -     | RTC.INT  | P0.30  | P7.3    |                             |
|          | -     | C2C.CLK  | P0.18  | P1.5    | msp.A0.CLK                  |
|          | -     | C2C.CoPi | P0.17  | P2.0    | msp.A0.CoPi                 |
|          | -     | C2C.CiPo | P0.14  | P2.1    | msp.A0.CiPo                 |
|          | -     | C2C.PSel | P0.22  | P1.4    | msp.A0.PSel                 |
|          |       | C2C.GPIO | P0.15  | PJ.2    |                             |

**Note**:
- SHP-HDR Spec of Cape V2.5
- Testbed has still v2.4, 2024-08 - see table for target v1.0

## Verifying the PCBs

- first do a visual inspection (both sides)
  - backside should be complete
  - front side can have two caps DNP: big C14 @RTC & C9 in the middle (SW of MSP430)

### Assembly

- solder the 2x9-Pin-Header

### First Powerup

- 2 mA @ 3V on V_target without programming
- 0 mA @ 3V on 3V-Input

### Software-Prereqs

**NOTE**: all further tests are done on BBone

```Shell
cd ~
git clone https://github.com/orgua/shepherd-datalib
cd shepherd-datalib
git checkout dev
git pull

python3 ./extra/gen_firmwares.py
sudo python3 ./extra/gen_experiments.py
```

Put Target on BBone with Target on Port 1!

### Test all GPIO & LEDs

First test all used gpio with this fw-combo (msp toggles, nrf watches and reports via uart):

```Shell
sudo shepherd-sheep program -p A -m 1 -v 3 -t nrf52 /var/shepherd/content/fw/nes_lab/nrf52_testable/build.hex
sudo shepherd-sheep program -p A -m 2 -v 3 -t msp430 /var/shepherd/content/fw/nes_lab/msp430_testable/build.hex
sudo shepherd-sheep target-power -p A -v 3 --on
# new
sudo shepherd-sheep run /etc/shepherd/target_device_test1.yaml
```

NOTE: best done with interconnector that only routes: pwr1, serial, programming-pins, pwr2
Check UART output with logic analyzer or in shepherd recording.
Behavior is described [here](https://github.com/orgua/shepherd-targets/tree/main/nrf52_testable).

### Testing the Radio

```Shell
sudo shepherd-sheep program -p A -m 1 -v 3 -t nrf52 /var/shepherd/content/fw/nes_lab/nrf52_rf_test/build.hex
sudo shepherd-sheep program -p A -m 2 -v 3 -t msp430 /var/shepherd/content/fw/nes_lab/msp430_deep_sleep/build.hex
sudo shepherd-sheep target-power -p A -v 3 --on
# new
sudo shepherd-sheep run /etc/shepherd/target_device_test2.yaml
```

Behavior is described [here](https://github.com/orgua/shepherd-targets/tree/main/nrf52_rf_test).

### Testing Power-consumption during sleep

```Shell
sudo shepherd-sheep program -p A -m 1 -v 3 -t nrf52 /var/shepherd/content/fw/nes_lab/nrf52_deep_sleep/build.hex
sudo shepherd-sheep program -p A -m 2 -v 3 -t msp430 /var/shepherd/content/fw/nes_lab/msp430_deep_sleep/build.hex
# new
sudo shepherd-sheep run /etc/shepherd/target_device_test3.yaml
```

## Assembled Units

- visual inspection -> reflow fails:
  - A: crystal on ABx & MSP, one R240 on back
  - B: crystal on MSP,
  - C: crystal on ABx & nRF
- PowerUp
  - C: 3-4 mA on VTarget, instead of 2 mA
- Programming -> A, B fully responding
- Testable-FW
  - many shorts or permanent-high GPIO
- RF-Test - 1 m away in Doughnut-Pattern & 1 m above
  - A: -56 dBm in, -49 dBm above (SMA-Port loosely attached)
  - B: -56 dBm in, -48 dBm above
  - C: -50 dBm in, -52 dBm above
  - C: -47 dBm above (soldered SMA)
  - Target 7 with Stub-Antenna: -64 dBm in, -62 dBm above
  - Target 18 with Chip-Antenna: -67 to -72 dBm in, -69 to -72 dBm above
  - Various far points in flat show: 80-100 with chip antenna, 85-90 with stub, 65-83 with dedicated Antenna

```A
GPIO WATCHER
Missing: 2 12         -> GPIO3, LED2
Always:  5 8 10 [14]  -> GPIO6, GPIO9, PH
              1
          1   1
        1 1   1
     1  1 1   1
     1  1 11  1
1    1  1 1   1
 1   1  1 1   1
   1 1  1 1   1
    11  1 1   1
     11 1 1   1
     1 11 1   1
     1  1 1   1
     1  111   1
     1  1 1   1
     1  1 1
     1  1 1  1
     1  1 1   1
     1  1 1     1
     1  1 1      1
     1  1 1       1
     1  1 1        1
     1  1 1         1
     1  1 11
     1  1 1
```

```B
GPIO WATCHER
Missing: 2 12 15
Always:  5 8 9 13 [14]
     1       11
     1  1    11
     1  1 1  11
     1  1    11
     1  11   11
     1  11 1 11
1    1  11   11
 1   1  11   11
   1 1  11   11
    11  11   11
     1  11   11
     11 11   11
     1 111   11
     1  11   11
     1  111  11
     1  11   11
     1  11   1
     1  11   11
     1  11   1
     1  11   1  1
     1  11   1   1
     1  11   1    1
     1  11   1     1
     1  11   1      1
     1  11 1 1
     1  11   11
     1  11 1 11
```

```C
GPIO WATCHER
Missing: none
Always:  [3] 5 9 [13]
   1
   1     1
   1 1   1
   1 1   1 1
   1 1   1
   1 1   1  1
   1 1   1  11
   1 1   1   1
   1 1   1  11
   1 1   1   1
   1 1   1  11
   1 1   1   1
     1   1   1
1    1   1   1
     1   1   1
     1   1  11
     1   1   1
 1   1   1   1
     1   1   1
     1   1  11
     1   1   1
  1  1   1   1
     1   1   1
     1   1  11
     1   1   1
   1 1   1   1
     1   1   1
     1   1  11
     1   1   1
    11   1   1
     1   1   1
     1   1  11
     1   1   1
     1   1  11
     1   1   1
     11  1   1
     1   1   1
     1   1  11
     1   1   1
     1 1 1   1
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
Received all 21 shared pins!!
```

## Bugs, Changes, Improvements

### Changes from prev Version

- two bat-status pins from cape would be better
    - goal: offer hysteresis - working good for riotee so far
    - second goal: compatibility with riotee-SDK for targets
- shared gpio would benefit from external PU/PD-Resistors, so current mcu-code can be more independent
    - problem: msp430 is reacting with high currents for floating pins
    - current solution: activate internal PD-Res in msp430 - at least for our sleep- & FRAM-firmware
- add a system to identify pcb? OW-nodeid or i2c-rom?
- ditch PAN1780 module to allow an external antenna (rf-performance of pan-module is sub-par)

#### Details

- additional parts to order
  - rpi pico - https://www.mouser.de/ProductDetail/Raspberry-Pi/SC0915?qs=T%252BzbugeAwjgnLi4azxXVFA%3D%3D
  - rpi pico H https://www.mouser.de/ProductDetail/Raspberry-Pi/SC0917?qs=T%252BzbugeAwjjvYEYcRJk%252Bxw%3D%3D
  - rpi pico W https://www.mouser.de/ProductDetail/Raspberry-Pi/SC0918?qs=T%252BzbugeAwjj9dgdBLZSmdg%3D%3D
  - rpi 5 https://www.mouser.de/ProductDetail/Raspberry-Pi/SC1112?qs=HoCaDK9Nz5c86n0i5EQ%2FPA%3D%3D
  - Antenna https://www.mouser.de/c/passive-components/antennas/?q=antenna%20sma&minimum%20frequency=2.4%20GHz%7C~2.41%20GHz~~2.45%20GHz&instock=y&NewSearch=1&rp=passive-components%2Fantennas%7C~Minimum%20Frequency&sort=pricing
  - Antenna refinement https://www.mouser.de/c/passive-components/antennas/?q=antenna%20sma&antenna%20connector%20type=SMA%20Connector%7C~SMA%20Male~~SMA%20Plug&maximum%20frequency=2.48%20GHz~~2.5%20GHz&minimum%20frequency=2.4%20GHz%7C~2.41%20GHz~~2.45%20GHz&instock=y&sort=pricing&NewSearch=1&rp=passive-components%2Fantennas%7C~Minimum%20Frequency%7C~Maximum%20Frequency%7C~Antenna%20Connector%20Type
  - HDR2x10 RM2 737-2PH2-20-UA
  - rare cape-parts
- gpio.9 is now dedicated gpio and not bat_OK anymore (free from LED.0)
- gpio.10 was LED.1, is now LED.0
- `VCAP_SENSE` was floating, now V_Target
  - https://github.com/NessieCircuits/Riotee_MSP430Fram/blob/main/src/main.c
  - https://github.com/NessieCircuits/Riotee_SDK/blob/main/core/include/riotee.h
  - `PIN_VCAP_SENSE`, `AIN_VCAP_SENSE` are configured, but unused by riotee (FRAM-FW & SDK)
- `PIN_MAX_INT` is left floating (unchanged) as it is configured, but unused by SDK & not avail on target
- discrete nRF52 IC,
  - Riotee: NRF52833-CJAA (+direction finding)
  - Targetv11: 52840 (+matter) -> Choose this one
  - CJAA => WLCS 3.2x3.2 mm
  - QIAA => aQFN73 7x7mm -> Choose this one
  - QDAA => QFN40
  - CFAA => WLCSP-44
- switch ClockCrystal from 20 ppm to 5 ppm
- LED.1 is unused -> removed
- 2x10 HDR -> RM2.0mm
- re-aligned gpios between observer & target
- nRF - 2 crystals
- also share threshold-control + max-int between MCUs (with 470R)
- SMA or uFL? -> SMA
- adapt capacities for crystals
- nRF - Antenna path - 630 um on L1/L4 are 50 Ohms,
  - both ant-traces are < 5 mm and therefore well below 10% of 2.4 GHz wavelength
- add antenna to schematic
- replace msp430 128kb (-FR5962) with riotees 256kb (-FR5994),

Skipped:
- PD-Res for internal Pins - 10 M?

### Riotee-SDK-patching

- target uses nRF52840 instead of Riotees -833
- main makefile specifies `NRF_DEV_NUM`
- Size of FRAM auto-adjust? -> main makefile `RIOTEE_RAM_RETAINED_SIZE`, `RIOTEE_STACK_SIZE`
- type of nRF relevant? -> main Makefile `NRF_DEV_NUM`

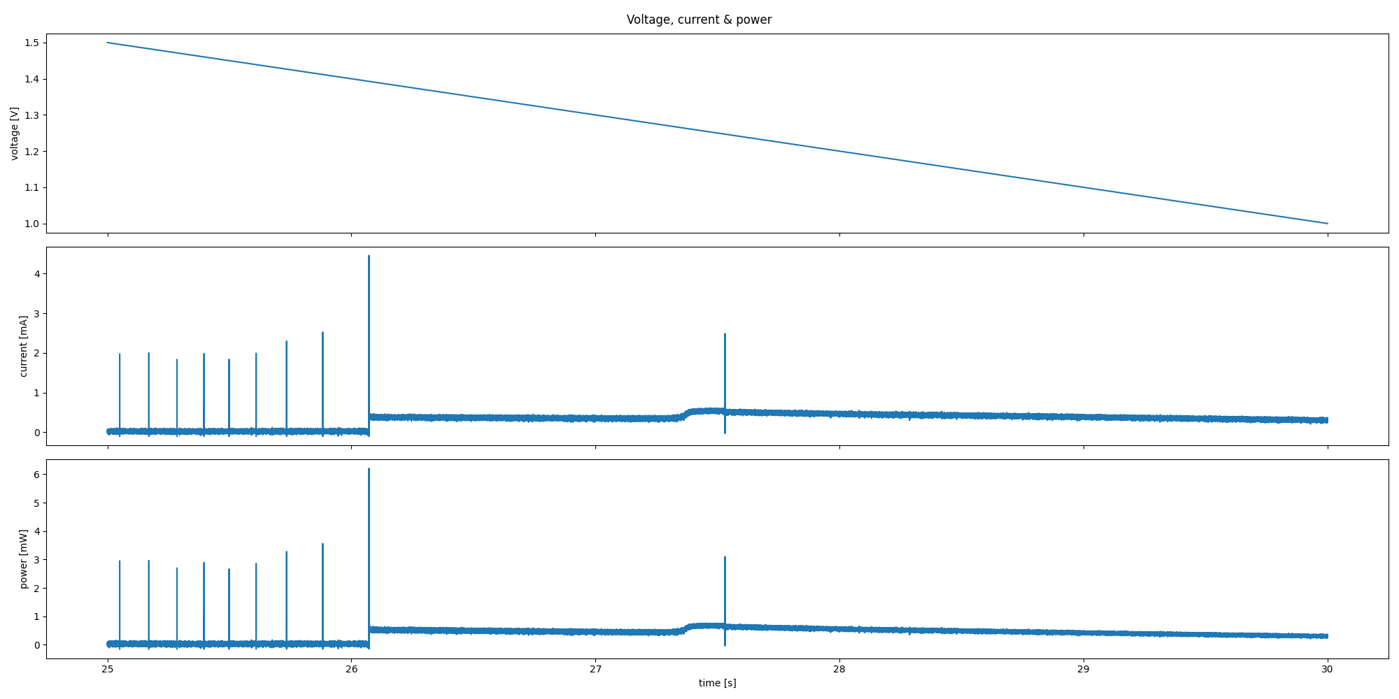
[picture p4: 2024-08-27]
hardware/shepherd_nRF_FRAM_Target_v1.3/emu_ramp.plot_25s000_to_30s000.png

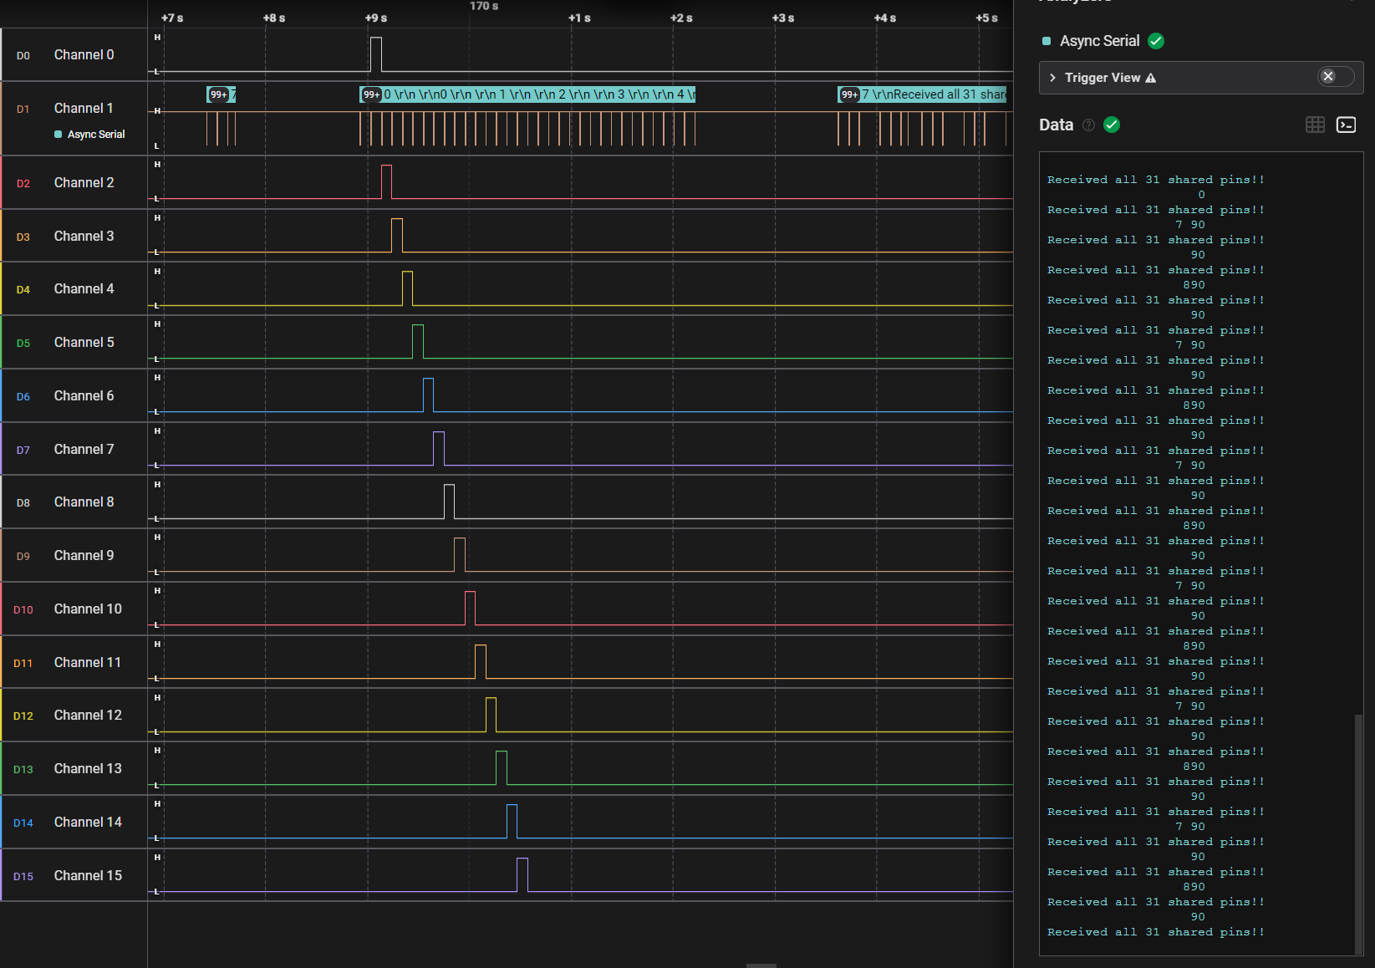
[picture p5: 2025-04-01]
hardware/shepherd_nRF_FRAM_Target_v1.3/Logic_all_pins.png

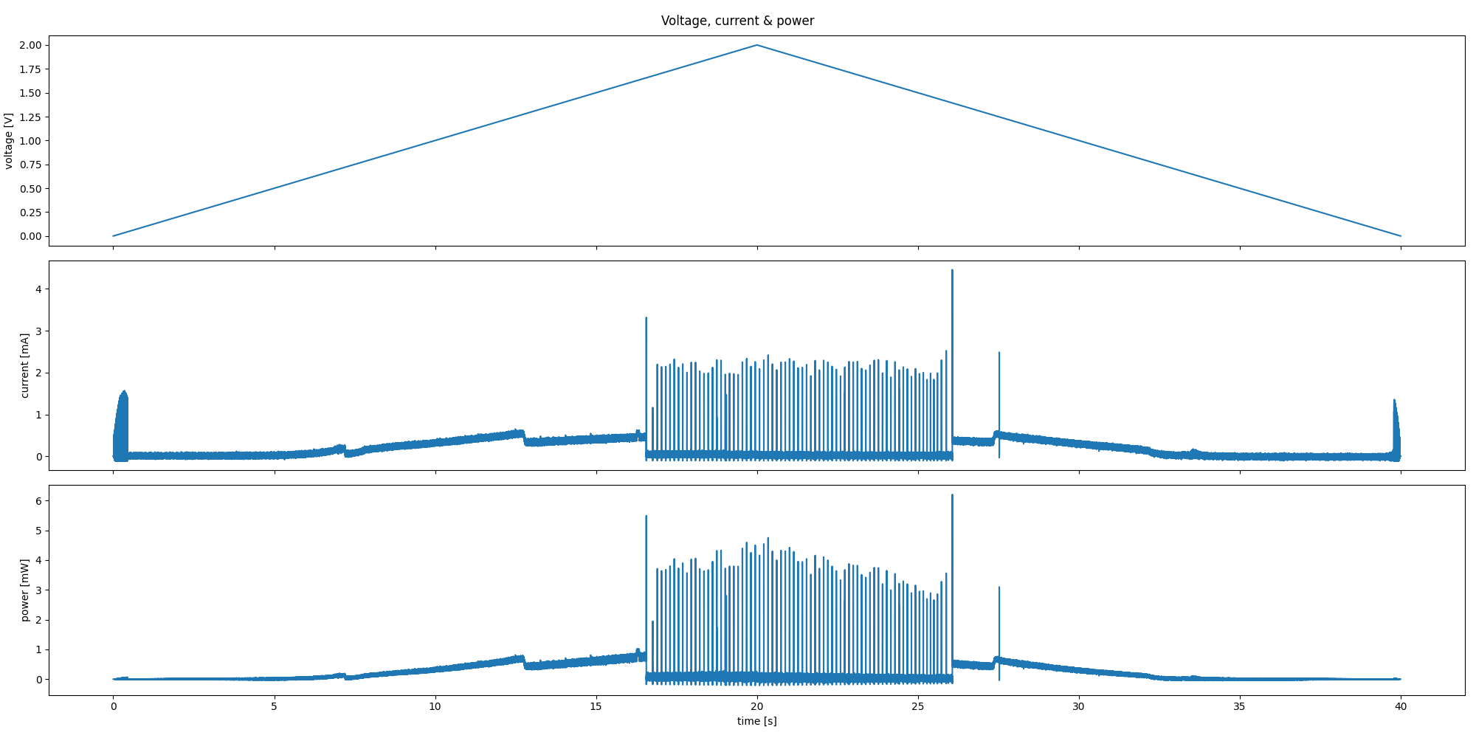
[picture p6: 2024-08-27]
hardware/shepherd_nRF_FRAM_Target_v1.3/emu_ramp.plot_0s000_to_40s000.png

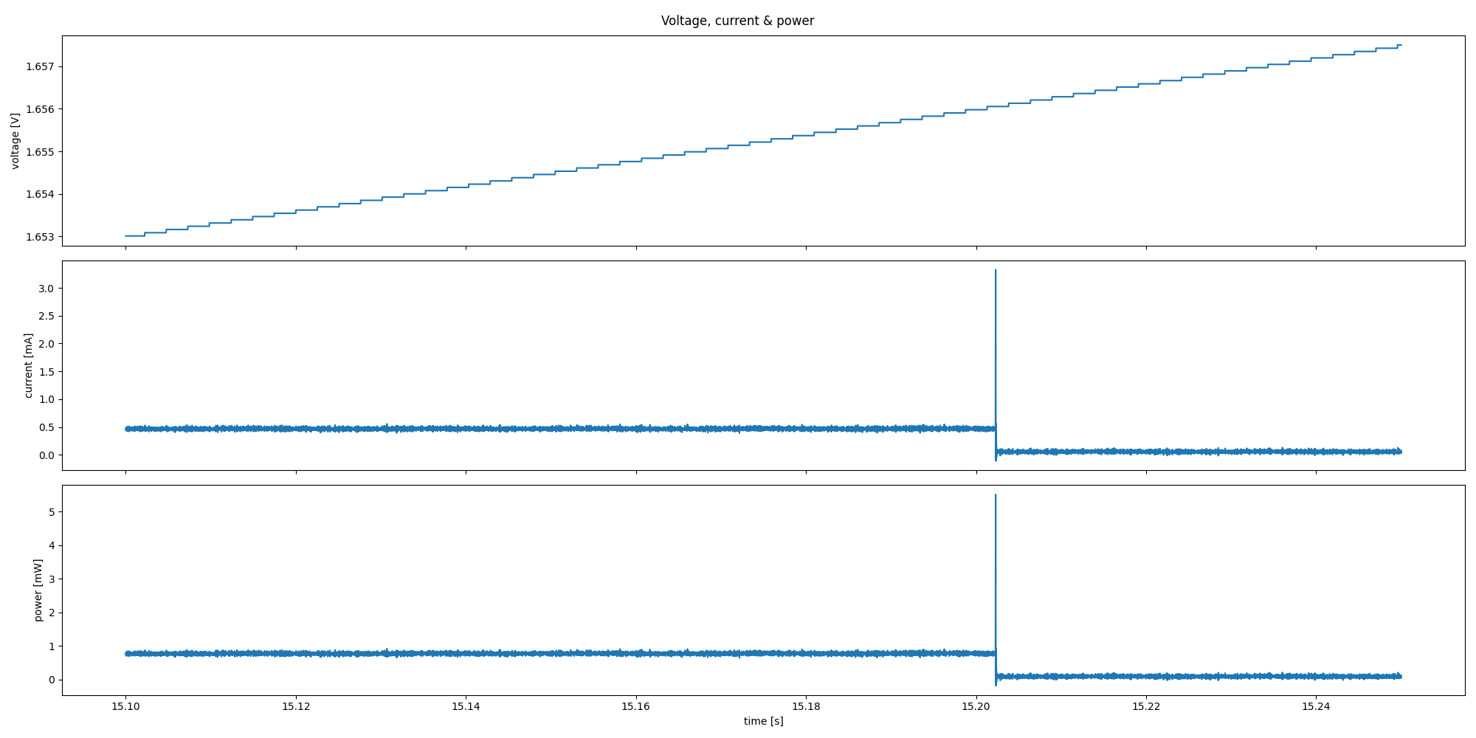
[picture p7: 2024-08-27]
hardware/shepherd_nRF_FRAM_Target_v1.3/emu_ramp2.plot_15s100_to_15s250.png

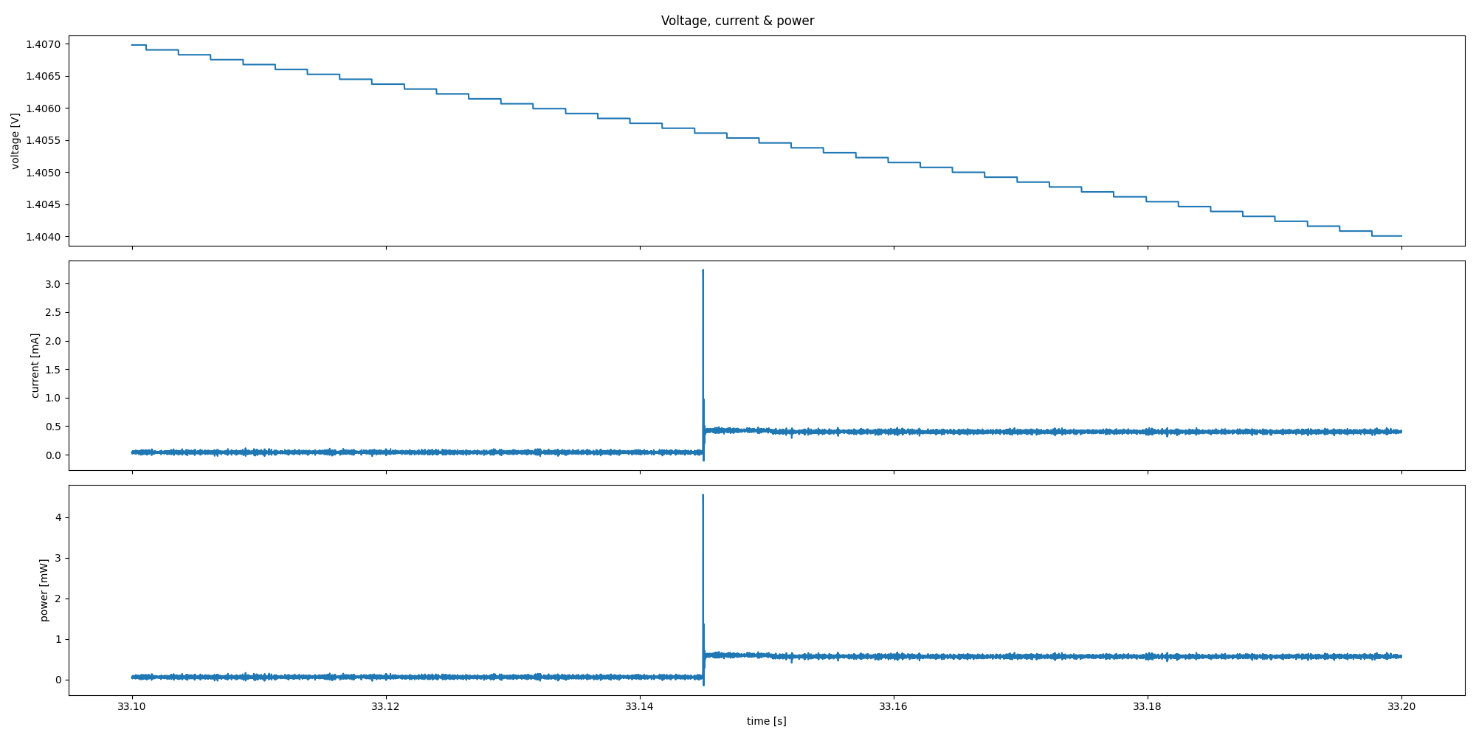
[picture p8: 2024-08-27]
hardware/shepherd_nRF_FRAM_Target_v1.3/emu_ramp2.plot_33s100_to_33s200.png

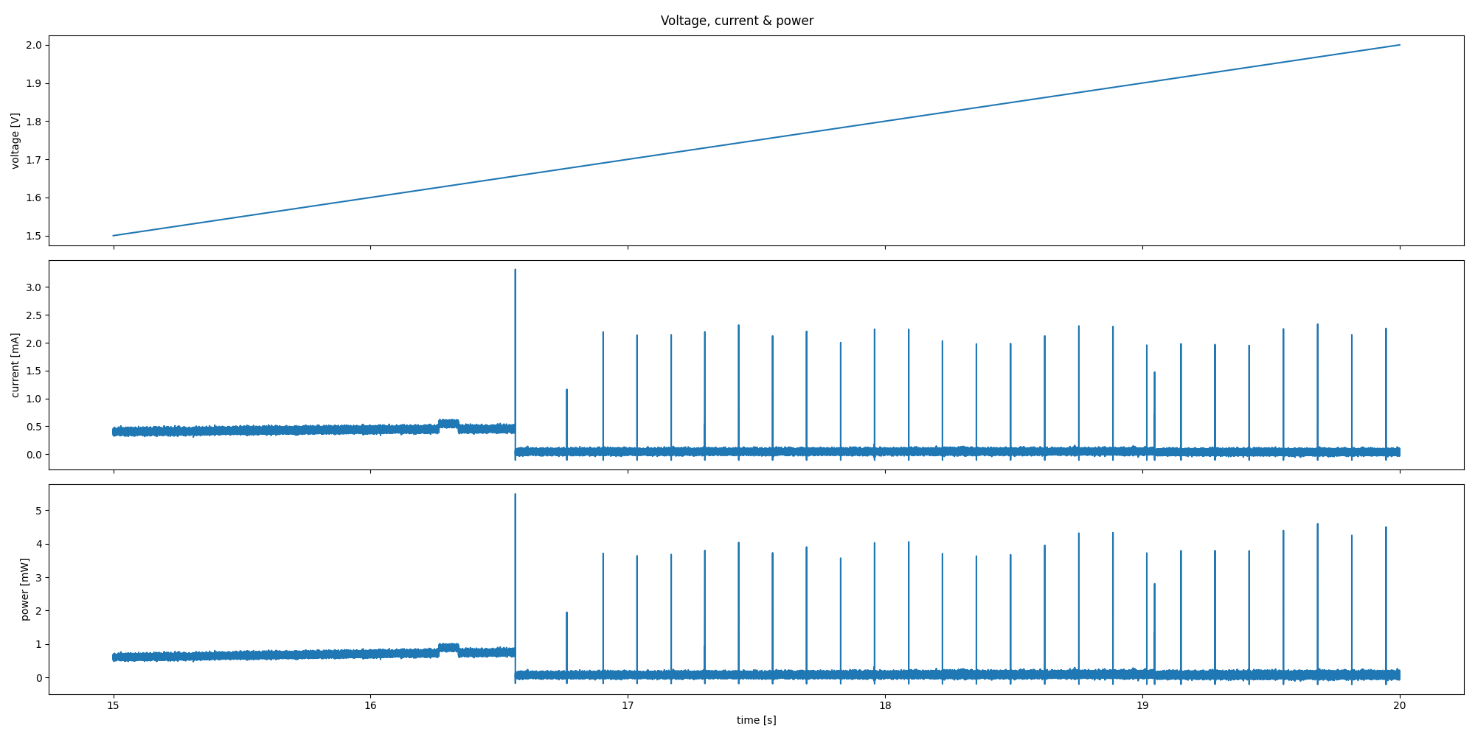
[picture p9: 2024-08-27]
hardware/shepherd_nRF_FRAM_Target_v1.3/emu_ramp.plot_15s000_to_20s000.png

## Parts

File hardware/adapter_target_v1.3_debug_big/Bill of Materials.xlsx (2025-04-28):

Comment | Designator | Footprint | LibRef | Quantity | Manufacturer | Manufacturer PN | Distributer | Distributer PN | Price n10 [€]
P_HSEC8-120-Edge | P1 | P_HSEC8-120_edge | .P_HSEC8-120-Edge | 1 | Samtec |  | Mouser
P_HSEC8-120-01-S-DV | P2 | P_HSEC8-120-01-S-DV | .P_HSEC8-120-01-S-DV | 1 | Samtec | HSEC8-120-01-L-DV-A-K-TR | Mouser | 200-HSEC812001LDVAKT | 3.17
P_HDR_2x13_2.54mm | P? | P_Pinheader_2x13_R2.54mm_pressfit | .P_HDR_2x13_2.54mm | 1 |  |  | Mouser

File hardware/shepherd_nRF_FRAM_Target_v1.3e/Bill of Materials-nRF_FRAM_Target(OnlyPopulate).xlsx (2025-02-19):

Comment | Designator | Footprint | LibRef | Quantity | Manufacturer | Manufacturer PN | Distributer | Distributer PN | Price n10 [€] | Q30 |  | Qorder | Diff
C_0402_1uF_10V_X7R | C1, C13, C18, C29 | CAPC1005X06 | .C_0402_1uF_X7R_10V | 4 | Murata | GRM155C71A105KE11D | Mouser | 81-GRM155C71A105KE1D | 0.036 | 120 | 81-GRM155C71A105KE1D | 200 | 80
C_0402_100nF_10V_X7G | C2, C3, C4, C5, C12, C14, C16, C17, C19, C23, C30, C31, C32 | CAPC1005X06 | .C_0402_100nF_10V | 13 | Murata | GRM155R71A104KA01D | Mouser | 81-GRM155R71A104KA1D | 0.019 | 390 | 81-GRM155R71A104KA1D | 500 | 110
C_0402_1pF_50V_NP0_RF | C6 | CAPC1005X06 | .C_0402_1pF_50V_NP0_RF | 1 | Murata | GJM1555C1H1R0JB01D | Mouser | 81-GJM1555C1H1R0JB1D | 0.056 | 30 | 81-GJM1555C1H1R0JB1D | 200 | 170
C_0402_1.2pF_50V_NP0 | C7 | CAPC1005X06 | .C_0402_1.2pF_50V_NP0_RF | 1 | Murata | GJM1555C1H1R2JB01D | Mouser | 81-GJM1555C1H1R2JB1D | 0.046 | 30 | 81-GJM1555C1H1R2JB1D | 200 | 170
C_0402_12pF_10V_NP0 | C8, C9, C10, C11, C21, C22, C27, C28 | CAPC1005X06 | .C_0402_12pF_10V_NP0 | 8 | Vishay | VJ0402A120JXQPW1BC | Mouser | 77-VJ0402A120JXQPBC | 0.08 | 240 | 77-VJ0402A120JXQPBC | 300 | 60
C_0402_820pF_50V_NP0 | C15 | CAPC1005X06 | .C_0402_820pF_50V_NP0 | 1 | Murata Electronics | GRM1555C1H821JA01J | Mouser | 81-GRM1555C1H821JA1J | 0.03 | 30 | 81-GRM1555C1H821JA1J | 200 | 170
C_0402_1nF_50V_NP0 | C20 | CAPC1005X06 | .C_0402_1nF_50V | 1 | Murata | DNP | Mouser | 81-GRM1555C1H102JA1D | DNP | 30 |  |  | -30
C_1206_47uF_10V_X5R | C24 | CAPC3216X18 | .C_1206_47uF_10V | 1 | Taiyo Yuden | LMK316ABJ476ML-T | Mouser | 963-LMK316ABJ476ML-T | 0.23 | 30 | 963-LMK316ABJ476ML-T | 60 | 30
C_0402_47pF_50V_NP0 | C26 | CAPC1005X06 | .C_0402_47pF_50V | 1 | Kemet | C0402C470K5GACTU | Mouser | 80-C0402C470K5G | 0.01 | 30 | 80-C0402C470K5G | 200 | 170
D_LED_0603_Amber | D1 | DIOM1608X02N Orange | .D_LED_0603_Amber | 1 | Wuerth | 150060AS75000 | Mouser | 710-150060AS75000 | 0.12 | 30 | 710-150060AS75000 | 50 | 20
D_LED_0603_Red | D2 | DIOM1608X02N Red | .D_LED_0603_Red | 1 | Wuerth | 150060SS55040 | Mouser | 710-150060SS55040 | 0.14 | 30 | 710-150060SS55040 | 50 | 20
PMEG10010ELR | D3 | SODFL350X110-2N | .D_SOD123W_710mV_1A | 1 | Nexperia | PMEG10010ELRX | Mouser | 771-PMEG10010ELRX | 0.24 | 30 | 771-PMEG10010ELRX | 100 | 70
LQG15HZ4N7C02D | L1 | IND1005X06 | .L_0402_4.7n_700mA | 1 | Murata | LQG15HZ4N7C02D | Mouser | 81-LQG15HZ4N7C02D | 0.05 | 30 | 81-LQG15HZ4N7C02D | 60 | 30
LQG15HZ2N2C02D | L2 | IND1005X06 | .L_0402_2.2n_900mA | 1 | Murata | LQG15HZ2N2C02D | Mouser | 81-LQG15HZ2N2C02D | 0.05 | 30 | 81-LQG15HZ2N2C02D | 60 | 30
ANT RF_SMA_2.44GHz | M1 |  | ANT RF_SMA_2.44GHz | 1 | TE | ANT-2.4-LCW-SMA | Mouser | 712-ANT-2.4-LCW-SMA | 3.09 | 30 | 712-ANT-2.4-LCW-SMA | 20 | -10
P_RF_SMA_Edge-Con | P1 | P_RF_SMA_Edge | .P_RF_SMA_Edge_Con | 1 | RF Solutions | CON-SMA-EDGE-S | Mouser | 223-CON-SMA-EDGE-S | 1.95 | 30 | 223-CON-SMA-EDGE-S | 20 | -10
P_HSEC8-120-Edge | P2 | P_HSEC8-120_edge | .P_HSEC8-120-Edge | 1 | Samtec |  | Mouser |  |  | 30 |  |  | -30
R_0402_240R | R1, R2, R3, R4, R5, R6, R7, R8, R9, R10, R11, R12, R13, R14, R17, R18, R19, R20, R21, R22, R24, R26, R29, R30, R31, R32, R33, R34, R35, R37, R39, R40, R41, R43, R45, R46, R47, R48, R49, R50, R51, R52, R53, R54, R55, R56, R58, R60, R62, R63, R68, R69 | RESC1005X04 | .R_0402_240R | 52 | Panasonic | ERJ-2GEJ241X | Mouser | 667-ERJ-2GEJ241X | 0.02 | 1560 | 667-ERJ-2GEJ241X | 2000 | 440
R_0402_470R | R15, R16, R23, R25, R27, R28, R36, R38, R42, R44, R57, R59 | RESC1005X04 | .R_0402_470R_1% | 12 | Panasonic | ERJ-2RKF4700X | Mouser | 667-ERJ-2RKF4700X | 0.028 | 360 | 667-ERJ-2RKF4700X | 500 | 140
R_0402_47k | R61 | RESC1005X04 | .R_0402_47k | 1 | Panasonic | ERJ-2GEJ473X | Mouser | 667-ERJ-2GEJ473X | 0.03 | 30 | 667-ERJ-2GEJ473X | 200 | 170
R_0402_1k | R64 | RESC1005X04 | .R_0402_1k | 1 | Panasonic | ERJ-2GEJ102X | Mouser | 667-ERJ-2GEJ102X | 0.02 | 30 | 667-ERJ-2GEJ102X | 200 | 170
R_0402_100R | R65 | RESC1005X04 | .R_0402_100R | 1 | Panasonic | ERJ-2GEJ101X | Mouser | 667-ERJ-2GEJ101X | 0.02 | 30 | 667-ERJ-2GEJ101X | 200 | 170
R_0402_1M | R66, R67, R72 | RESC1005X04 | .R_0402_1M | 3 | Panasonic | ERJ-2GEJ105X | Mouser | 667-ERJ-2GEJ105X | 0.02 | 90 | 667-ERJ-2GEJ105X | 200 | 110
R_0402_100k_1% | R70, R71, R74 | RESC1005X04 | .R_0402_100k | 3 | Panasonic | ERJ-2RKF1003X | Mouser | 667-ERJ-2RKF1003X | 0.02 | 90 | 667-ERJ-2RKF1003X | 200 | 110
R_0402_10k | R73 | RESC1005X04 | .R_0402_10k | 1 | Panasonic | ERJ-2GEJ103X | Mouser | 667-ERJ-2GEJ103X | 0.02 | 30 | 667-ERJ-2GEJ103X | 200 | 170
BSH105 | T1, T2 | SOT95P230X110-3N | .T_BSH105 | 2 | Nexperia | BSH105,215 | Mouser | 771-BSH105215 | 0.21 | 60 | 771-BSH105215 | 100 | 40
nRF52840-QIAA | U1 | BGAS73C25P24X24_700X700X85 | nRF52840-QIAA | 1 | Nordic | nRF52840-QIAA | Mouser | 949-NRF52840-QIAA-R | 5.29 | 30 | 949-NRF52840-QIAA-R | 30 | 0
MSP430FR5994IZVWR | U2 | BGA121C50P11X11_600X600X100 | MSP430FR5994IZVW | 1 | Texas Instruments | MSP430FR5994IZVWR | Mouser | 595-P430FR5994IZVWR | 7.24 | 30 | 595-P430FR5994IZVWR | 30 | 0
AB1805 | U3 | QFN50P300X300X100_HS-17N | AB1805 | 1 | Abracon | AB1805-T3 | Mouser | 815-AB1805-T3 | 1.72 | 30 | 815-AB1805-T3 | 30 | 0
TS5A3167DCKR | U4 | SOT65P210X110-5N | TS5A3167DCKR | 1 | Texas Instruments | TS5A3167DCKR | Mouser | 595-TS5A3167DCKR | 0.302 | 30 | 595-TS5A3167DCKR | 30 | 0
MCP6546T-I/LT | U5 | SOT65P210X110-5N | MCP6546 | 1 | Microchip | MCP6546T-I/LT | Mouser | 579-MCP6546T-I/LT | 0.307 | 30 | 579-MCP6546T-I/LT | 30 | 0
ECX-.327-CDX-1293 | X1, X3, X4 | XTAL_ECS-32x15 | .X_ECX-.327-CDX-1293 | 3 | ECS | ECX-.327-CDX-1293 | Mouser | 520-ECX-.327CDX-1293 | 0.43 | 90 | 520-ECX-.327CDX-1293 | 100 | 10
ECS-320-12-37B2-7KM | X2 | XTAL_ECS_20x16_4L | .X_ECS-320-12-37B2-7KM | 1 | ECS | ECS-320-12-37B2-7KM-TR | Mouser | 520-320-12-37B27KMTR | 0.26 | 30 | 520-320-12-37B27KMTR | 50 | 20
 |  |  |  |  |  |  |  |  |  |  |  | 650.77 €

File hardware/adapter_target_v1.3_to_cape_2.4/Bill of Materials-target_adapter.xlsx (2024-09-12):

Comment | Designator | Footprint | LibRef | Quantity | Manufacturer | Manufacturer PN | Distributer | Distributer PN | Price n10 [€]
P_HDR_2x9_2.54mm_socket | P1 | P_Pinheader_2x9_R2.54mm_pressfit | .P_HDR_2x9_2.54mm_female | 1 | Samtech | SSQ-109-02-S-D-RA | Mouser | 200-SSQ10902SDRA | 4,24
P_HSEC8-120-01-S-DV | P2 | P_HSEC8-120-01-S-DV | .P_HSEC8-120-01-S-DV | 1 | Samtec | HSEC8-120-01-L-DV-A-K-TR | Mouser | 200-HSEC812001LDVAKT | 3.17
R_0402_10R | R1 | RESC1005X04 | .R_0402_10R | 1 | Panasonic | ERJ-2GEJ100X | Mouser | 667-ERJ-2GEJ100X | 0.02

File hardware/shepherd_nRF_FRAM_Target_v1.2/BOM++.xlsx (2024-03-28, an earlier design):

Comment | Quantity | Manufacturer | Manufacturer PN | Distributer | Distributer PN | Price n10 [€] | Q25 | Distributer PN | QE | PriceAll
C_0402_100nF_10V | 11 | Murata | GCM155R71A104KA55D | Mouser | 81-GCM155R71A104K5D | 0.03 | 275 | 81-GCM155R71A104K5D | 500 | 8
C_0402_1uF_25V | 3 | Murata | GRM155R61E105KA12J | Mouser | 81-GRM155R61E105KA2J | 0.06 | 75 | 81-GRM155R61E105KA2J | 100 | 1.3
C_0402_12pF_10V_NP0 | 6 | Vishay | VJ0402A120JXQPW1BC | Mouser | 77-VJ0402A120JXQPBC | 0.08 | 150 | 77-VJ0402A120JXQPBC | 200 | 5
C_1206_47uF_10V | 1 | Taiyo Yuden | LMK316ABJ476ML-T | Mouser | 963-LMK316ABJ476ML-T | 0.23 | 25 | 963-LMK316ABJ476ML-T | 50 | 13.6
C_0402_47pF_50V | 1 | Kemet | C0402C470K5GACTU | Mouser | 80-C0402C470K5G | 0.01 | 25 | 80-C0402C470K5G | 100 | 0.6
C_0402_1uF_10V_X7R | 1 | Murata | GCM155C71A105KE38D | Mouser | 81-GCM155C71A105KE8D | 0.05 | 25 | 81-GCM155C71A105KE8D | 100 | 2.4
C_0402_820pF_50V | 1 | Murata Electronics | GRM1555C1H821JA01J | Mouser | 81-GRM1555C1H821JA1J | 0.03 | 25 | 81-GRM1555C1H821JA1J | 50 | 1.65
C_0402_800fF_50V | 1 | Murata Electronics | GCM1555C1HR80WA16D | Mouser | 81-GCM1555C1HR80WA6D | 0.083 | 25 | 81-GCM1555C1HR80WA6D | 50 | 4.15
C_0402_500fF_50V | 1 | Murata Electronics | GCM1555C1HR50WA16D | Mouser | 81-GCM1555C1HR50WA6D | 0.083 | 25 | 81-GCM1555C1HR50WA6D | 50 | 4.15
D_LED_0603_Amber | 1 | Wuerth | 150060AS75000 | Mouser | 710-150060AS75000 | 0.12 | 25 | 710-150060AS75000 | 50 | 6.6
D_SOD123W_710mV_1A | 1 | Nexperia | PMEG10010ELRX | Mouser | 771-PMEG10010ELRX | 0.24 | 25 | 771-PMEG10010ELRX | 50 | 13.4
D_LED_0603_Red | 1 | Wuerth | 150060SS55040 | Mouser | 710-150060SS55040 | 0.14 | 25 | 710-150060SS55040 | 50 | 8
L_0402_4.7n_700mA | 1 | Murata | LQG15HZ4N7C02D | Mouser | 81-LQG15HZ4N7C02D | 0.05 | 25 | 81-LQG15HZ4N7C02D | 50
P_HDR_2x10_2.0mm_socket | 1 | Samtech | SQT-110-01-F-D-RA | Mouser | 200-SQT11001FDRA | 2,69 | 25 | 200-SQT11001FDRA | 25
P_RF_SMA_Edge-Con | 1 | RF Solutions | CON-SMA-EDGE-S | Mouser | 223-CON-SMA-EDGE-S | 1.95 | 25 | 223-CON-SMA-EDGE-S | 25
R_0402_1k | 1 | Panasonic | ERJ-2GEJ102X | Mouser | 667-ERJ-2GEJ102X | 0.02 | 25 | 667-ERJ-2GEJ102X | 50
R_0402_1M | 2 | Panasonic | ERJ-2GEJ105X | Mouser | 667-ERJ-2GEJ105X | 0.02 | 50 | 667-ERJ-2GEJ105X | 100
R_0402_47k | 1 | Panasonic | ERJ-2GEJ473X | Mouser | 667-ERJ-2GEJ473X | 0.03 | 25 | 667-ERJ-2GEJ473X | 50
R_0402_240R | 40 | Panasonic | ERJ-2GEJ241X | Mouser | 667-ERJ-2GEJ241X | 0.02 | 1000 | 667-ERJ-2GEJ241X | 1000
R_0402_470R | 12 | Panasonic | ERJ-2RKF4700X | Mouser | 667-ERJ-2RKF4700X | 0.028 | 300 | 667-ERJ-2RKF4700X | 300
R_0402_100R | 1 | Panasonic | ERJ-2GEJ101X | Mouser | 667-ERJ-2GEJ101X | 0.02 | 25 | 667-ERJ-2GEJ101X | 50
T_BSH105 | 2 | Nexperia | BSH105,215 | Mouser | 771-BSH105215 | 0.21 | 50 | 771-BSH105215 | 50
UD_nRF52840 | 1 | Nordic | nRF52840-QIAA | Mouser | 949-NRF52840-QIAA-R | 5.29 | 25 | 949-NRF52840-QIAA-R | 30
UD_MSP430FR5962 | 1 | Texas Instruments | MSP430FR5962IZVWR | Mouser | 595-SP430FR5962IZVWR | 6.67 | 25 | 595-P430FR5994IZVWR | 30
UD_AB1805 | 1 | Abracon | AB1805-T3 | Mouser | 815-AB1805-T3 | 1.72 | 25 | 815-AB1805-T3 | 30
ECX-.327-CDX-1293 | 3 | ECS | ECX-.327-CDX-1293 | Mouser | 520-ECX-.327CDX-1293 | 0.43 | 75 | 520-ECX-.327CDX-1293 | 100
ECS-320-12-37B2-7KM | 1 | ECS | ECS-320-12-37B2-7KM-TR | Mouser | 520-320-12-37B27KMTR | 0.26 | 25 | 520-320-12-37B27KMTR | 30
 |  |  | RPI Pico | Mouser |  |  |  | 358-SC0915 | 5 | 18.6
 |  |  | RPI Pico W | Mouser |  |  |  | 358-SC0918 | 2 | 8
 |  |  | Rpi 5 | Mouser |  |  |  | 358-SC1112 | 3 | 223
 |  |  | Header | Mouser |  |  |  | 737-2PH2-20-UA | 50 | 14
 |  |  | Antenna | Mouser |  |  |  | 712-ANT-2.4-LCW-SMA | 20 | 62
 |  |  | LevelShift | Mouser |  |  |  | 771-74LVC2T45GT115 | 100 | 34
 |  |  | ADC | Mouser |  |  |  | 595-ADS8691IPW | 60 | 642
 |  |  | InAmp | Mouser |  |  |  | 584-AD8421BRMZ | 50 | 480
 |  |  |  |  |  |  |  |  |  | 1481.6
 |  |  |  |  |  |  |  |  |  | 654.4 | 32.72
 |  |  |  |  |  |  |  | https://www.mouser.de/ProjectManager/ProjectDetail.aspx?AccessID=a4bf255874
 |  |  |  |  |  |  |  | a4bf255874

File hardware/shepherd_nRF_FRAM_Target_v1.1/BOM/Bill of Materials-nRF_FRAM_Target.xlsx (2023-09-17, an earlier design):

Comment | Designator | Footprint | LibRef | Quantity | Manufacturer | Manufacturer PN | Distributer | Distributer PN | Price n10 [€]
C_0402_100nF_10V | C1, C3, C6, C8, C10, C13 | CAPC1005X06 | .C_0402_100nF_10V | 6 | Murata | GCM155R71A104KA55D | Mouser | 81-GCM155R71A104K5D | 0.03
C_0402_1uF_25V | C2, C7 | CAPC1005X06 | .C_0402_1uF_25V | 2 | Murata | GRM155R61E105KA12J | Mouser | 81-GRM155R61E105KA2J | 0.06
C_0402_12pF_10V_NP0 | C4, C5 | CAPC1005X06 | .C_0402_12pF_10V_NP0 | 2 | Vishay | VJ0402A120JXQPW1BC | Mouser | 77-VJ0402A120JXQPBC | 0.08
DNP | C9 | CAPC1005X06 DNP | .C_0402_1nF_50V | 1 | Murata | GRM1555C1H102JA01D | Mouser | 81-GRM1555C1H102JA1D | 0.02
C_1206_47uF_10V | C11 | CAPC3216X18 | .C_1206_47uF_10V | 1 | Taiyo Yuden | LMK316ABJ476ML-T | Mouser | 963-LMK316ABJ476ML-T | 0.23
C_0402_47pF_50V | C12 | CAPC1005X06 | .C_0402_47pF_50V | 1 | Kemet | C0402C470K5GACTU | Mouser | 80-C0402C470K5G | 0.01
DNP | C14 | CAPC3216X18 DNP | .C_1206_100uF_6V3 | 1 | Taiyo Yuden | JMK316ABJ107ML-T | Mouser | 963-JMK316ABJ107ML-T | 0.25
D_LED_0603_Amber | D1, D2 | DIOM1608X02N Orange | .D_LED_0603_Amber | 2 | Wuerth | 150060AS75000 | Mouser | 710-150060AS75000 | 0.12
D_SOD123W_710mV_1A | D3 | SODFL350X110-2N | .D_SOD123W_710mV_1A | 1 | Nexperia | PMEG10010ELRX | Mouser | 771-PMEG10010ELRX | 0.24
D_LED_0603_Red | D4 | DIOM1608X02N Red | .D_LED_0603_Red | 1 | Wuerth | 150060SS55040 | Mouser | 710-150060SS55040 | 0.14
P_HDR_2x9_2.54mm_socket | P1 | P_Pinheader_2x9_R2.54mm_female_angled | .P_HDR_2x9_2.54mm_female | 1 | Samtech | SSQ-109-02-S-D-RA | Mouser | 200-SSQ10902SDRA | 4,24
R_0402_1k | R1, R5 | RESC1005X04 | .R_0402_1k | 2 | Panasonic | ERJ-2GEJ102X | Mouser | 667-ERJ-2GEJ102X | 0.02
R_0402_1M | R2, R6, R7 | RESC1005X04 | .R_0402_1M | 3 | Panasonic | ERJ-2GEJ105X | Mouser | 667-ERJ-2GEJ105X | 0.02
R_0402_47k | R3 | RESC1005X04 | .R_0402_47k | 1 | Panasonic | ERJ-2GEJ473X | Mouser | 667-ERJ-2GEJ473X | 0.03
R_0402_240R | R4, R8, R9, R10, R11, R12, R13, R14, R15, R16, R17, R18, R19, R20, R21, R22, R23, R24, R25, R26, R27, R28, R29, R32, R33, R34, R37, R38, R39, R40, R41, R42, R43, R44, R46, R47, R49, R50 | RESC1005X04 | .R_0402_240R | 38 | Panasonic | ERJ-2GEJ241X | Mouser | 667-ERJ-2GEJ241X | 0.02
R_0402_470R | R30, R31, R35, R36, R45 | RESC1005X04 | .R_0402_470R_1% | 5 | Panasonic | ERJ-2RKF4700X | Mouser | 667-ERJ-2RKF4700X | 0.028
R_0402_100R | R48 | RESC1005X04 | .R_0402_100R | 1 | Panasonic | ERJ-2GEJ101X | Mouser | 667-ERJ-2GEJ101X | 0.02
T_BSH105 | T1, T2, T3 | SOT95P230X110-3N | .T_BSH105 | 3 | Nexperia | BSH105,215 | Mouser | 771-BSH105215 | 0.21
_ENW-89854A1KF | U1 | LGA81C110P13X7_1580X870X230 | PAN1780 | 1 | Panasonic | ENW-89854A1KF | Mouser | 667-ENW-89854A1KF | 9.50
UD_MSP430FR5962 | U2 | BGA121C50P11X11_600X600X100 | MSP430FR5962IZVW | 1 | Texas Instruments | MSP430FR5962IZVWR | Mouser | 595-SP430FR5962IZVWR | 6.67
UD_AB1805 | U3 | QFN50P300X300X100_HS-17N | AB1805 | 1 | Abracon | AB1805-T3 | Mouser | 815-AB1805-T3 | 1.72
CM8V-T1A-32.768 | X1, X2 | XTAL_CM8V-T1A | .X_CM8V-T1A-32.768 | 2 | Micro Crystal | CM8V-T1A-32.768kHz-9pF-20PPM-TA-QC | Mouser | 428-201410-MC01 | 0.484

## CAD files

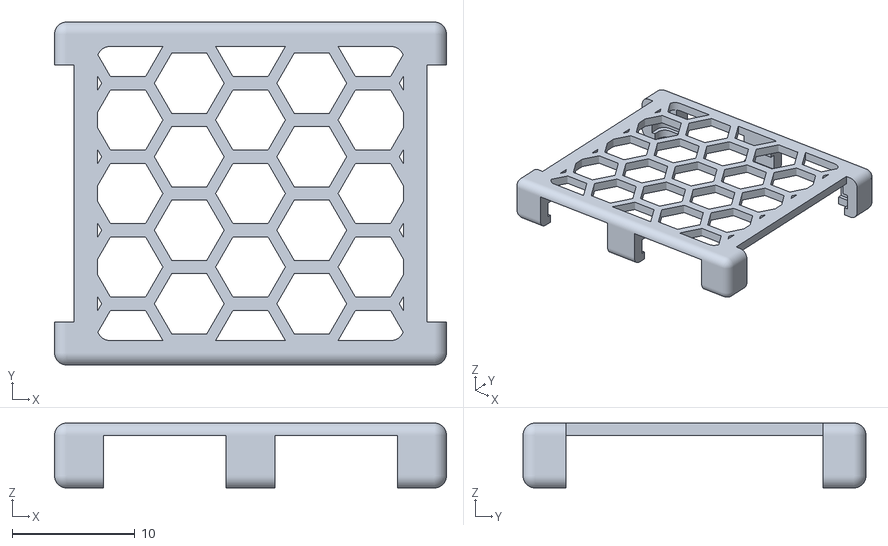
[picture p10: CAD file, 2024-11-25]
hardware/target_v1.3_cage/target_v13_cage.stl
32.0 x 28.0 x 5.30

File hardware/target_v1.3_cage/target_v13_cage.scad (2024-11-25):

pcb_x = 29.0;
pcb_y = 25.0;
pcb_z1 = 1.75;
pcb_z2 = 3.3;


// unregular cube
// 4 of the 12 edges are rounded
module round_cuboid(x,y,z,r,$fn=48)
{
    cube([x,y-2*r,z],center=true);
    cube([x-2*r,y,z],center=true);
    cube([x-2*r,y-2*r,z],center=true);

    translate([+x/2-r,+y/2-r,0]) cylinder(r=r,h=z,center=true);
    translate([+x/2-r,-y/2+r,0]) cylinder(r=r,h=z,center=true);
    translate([-x/2+r,+y/2-r,0]) cylinder(r=r,h=z,center=true);
    translate([-x/2+r,-y/2+r,0]) cylinder(r=r,h=z,center=true);
}

// unregular cube
// all 12 edges are rounded
module round_cuboid3(x,y,z,r,$fn=48)
{
    cube([x,y-2*r,z-2*r],center=true);
    cube([x-2*r,y,z-2*r],center=true);
    cube([x-2*r,y-2*r,z],center=true);

    translate([+x/2-r,+y/2-r,0]) cylinder(r=r,h=z-2*r,center=true);
    translate([+x/2-r,-y/2+r,0]) cylinder(r=r,h=z-2*r,center=true);
    translate([-x/2+r,+y/2-r,0]) cylinder(r=r,h=z-2*r,center=true);
    translate([-x/2+r,-y/2+r,0]) cylinder(r=r,h=z-2*r,center=true);

    translate([+x/2-r,0,+z/2-r]) rotate([90,0,0]) cylinder(r=r,h=y-2*r,center=true);
    translate([+x/2-r,0,-z/2+r]) rotate([90,0,0]) cylinder(r=r,h=y-2*r,center=true);
    translate([-x/2+r,0,+z/2-r]) rotate([90,0,0]) cylinder(r=r,h=y-2*r,center=true);
    translate([-x/2+r,0,-z/2+r]) rotate([90,0,0]) cylinder(r=r,h=y-2*r,center=true);

    translate([0,+y/2-r,+z/2-r]) rotate([0,90,0]) cylinder(r=r,h=x-2*r,center=true);
    translate([0,+y/2-r,-z/2+r]) rotate([0,90,0]) cylinder(r=r,h=x-2*r,center=true);
    translate([0,-y/2+r,+z/2-r]) rotate([0,90,0]) cylinder(r=r,h=x-2*r,center=true);
    translate([0,-y/2+r,-z/2+r]) rotate([0,90,0]) cylinder(r=r,h=x-2*r,center=true);

    translate([+(x/2-r),+(y/2-r),+(z/2-r)]) sphere(r=r);
    translate([+(x/2-r),+(y/2-r),-(z/2-r)]) sphere(r=r);
    translate([+(x/2-r),-(y/2-r),+(z/2-r)]) sphere(r=r);
    translate([+(x/2-r),-(y/2-r),-(z/2-r)]) sphere(r=r);
    translate([-(x/2-r),+(y/2-r),+(z/2-r)]) sphere(r=r);
    translate([-(x/2-r),+(y/2-r),-(z/2-r)]) sphere(r=r);
    translate([-(x/2-r),-(y/2-r),+(z/2-r)]) sphere(r=r);
    translate([-(x/2-r),-(y/2-r),-(z/2-r)]) sphere(r=r);
}


module target13()
{
    // cutouts
    union() {
        // PCB + Parts (large cutout)
        translate([0,0,pcb_z1/2]) round_cuboid(x=pcb_x+0.1, y=pcb_y+0.1, z=pcb_z1+0.1,r=1);
        translate([0,0,pcb_z2/2]) round_cuboid(x=pcb_x-2*0.6, y=pcb_y-2*0.6, z=pcb_z2,r=1);
        // cutout below
        translate([0,0,-pcb_z2/2]) round_cuboid(x=29-2*0.4, y=25-2*0.40, z=pcb_z2,r=1);

        // Connector
        translate([-pcb_x/2,0,3.3/2]) cube([10,21,3.3], center=true);
        translate([-(pcb_x+10-0.2)/2,0,3.3/2]) cube([10,21,20], center=true);
        translate([-pcb_x/2-0.2,0,-2]) cube([10,21,4], center=true);

        // SMA-Connector
        translate([+pcb_x/2,0,3.3/2]) cube([10,21,3.3], center=true);
        translate([+(pcb_x+10-0.2)/2,0,3.3/2]) cube([10,21,20], center=true);
        translate([+pcb_x/2-0.2,0,-2]) cube([10,21,4], center=true);

        // Side-cutouts
        translate([+7.0,0,0]) cube([10,pcb_y+10,2*pcb_z2], center=true);
        translate([-7.0,0,0]) cube([10,pcb_y+10,2*pcb_z2], center=true);
    }
}

module window_honey_neg()
{
    // honey comb top
    // easy way to tune line-thickness -> d_cylinder
    intersection () {
        translate([0,0,pcb_z2]) round_cuboid(x=pcb_x-4.0, y=pcb_y-1.0, z=pcb_z2, r=1);
        for (i = [-5:1:5], j=[-5:1:10]) {
            translate([i*5.0,i*3.0 + j*6,0]) cylinder(h=25, d=5.7, $fn=6);
        }
    }
}

module cage()
{
    difference () {
        translate([0,0,pcb_z2/2]) round_cuboid3(x=pcb_x+2*1.5, y=pcb_y+2*1.5, z=pcb_z2+2*1, r=1);
        window_honey_neg();
        target13();
    }
}


//target13();
//window_honey_neg();
cage();

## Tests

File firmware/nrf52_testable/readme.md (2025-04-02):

# nRF52 Testable

The app monitors shared GPIO pins and reports via uart upon detection.
This needs a second MCU that toggles these gpio (companion-firmware `/msp430_testable`).
Alternatively this FW can change the mode to toggling-behavior.

Other modes:

Print the index of the pin where the edge was detected over UART.
Simultaneously, it waits for incoming messages on the UART.
When receiving an ASCII encoded number between 0 and the number of configured pins,
the app sets the corresponding pin high for ~100us.

Edit the `pins` array and the UART pin definitions at the top of `src/main.c` to reflect your hardware.

## Functionality

### Mode 0 - Supervisor (default)

- monitor all shared GPIO and report activity via uart
- msp-testable-firmware is actor (gpio toggle, here mode 1)
- NOTE: requires special Header-Inter-connector that only routes pwr, uart tx, programming (pin 1, 2, 10, 13 - 18)
- NOTE 3: 115200 baud datarate

### Mode 1 - Actor

- Startup-Routine 1:
  - toggles LEDs, Pins on the shepherd target-port (without UART-TX), I2C pins, chip-to-chip (C2C) pins
  - blink / switch on each pin individually for 100 ms
- Startup-Routine 2: LEDs
  - switch each LED on for 100ms consecutive
  - (depending on node-id) >=8 repetitions
  - LED0:2 (Target v2.1)

### Mode >=2

- UART
    - P0_06 TX, _08 RX (Target v2.1, SDK)
    - listens and answers
    - should report when GPIOs are triggered
- GPIO
    - active: GPIO of shepherd target header (GPIO 0 to 6, 8, BATOK -> map to 0:8)
    - switch on for 100 us after receiving on UART ("(%u)\r\n")
- NOTE: 115200 baud datarate

## Example Output Mode 0

```uart
GPIO WATCHER (31 pins)
               56
0              56
               56
 1             56
               56
  2            56
               56
   3           56
               56
    4          56
               56
     5         56
               56
      6        56
               56
       7       56
               56
        8      56
               56
         9     56
               56
          0    56
               56
           1   56
               56
            2  56
               56
             3 56
               56
              456
               56
               567
               56
               56 8
               56
               56  9
               56
               56   0
               56
               56    1
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
Received all 31 shared pins!!
```

## Source

https://github.com/geissdoerfer/shepherd-nrf52-demo

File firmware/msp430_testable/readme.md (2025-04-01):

# Msp430 Testable

This is the companion-firmware for `/nrf_testable` to verify the hardware.
The firmware toggles all used & shared GPIOs and depends on a receiver / supervisor that verifies each pin.

Sequence:

- LEDs go first
- all pins of GPIO-Header
- shared I2C-Pins
- shared C2C-Pins (SPI)
- blink LEDs >8 times (reacts to SHEPHERD_NODE_ID) for 100 ms

## Functionality

- Startup-Routine 1:
  - toggles LEDs, Pins on the shepherd target-port (without UART-TX), I2C pins, Chip2chip (C2C) pins
  - blink / switch on each pin individually for 100 ms
- Startup-Routine 2: LEDs
  - switch each LED on for 100ms consecutive
  - (depending on node-id) >=8 repetitions
  - LED0:2 (Target v2.1)

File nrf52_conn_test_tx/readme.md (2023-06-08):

# nRF using TrafficBench to survey the

## TODO:

- auto generate schedule (sleep, trx, repeat)
- factor in TRX_PRE_DELAY and _POST_DELAY
- adapt uart-speed
- change GPI to use correct uart-pins
- look for other IO used by TB

## Source

https://gitlab.com/nes-lab/trafficbench

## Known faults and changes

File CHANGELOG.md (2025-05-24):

# Changelog

# v0.6.0

- extend documentation
- hardware - add more adapters (mostly for debug)
- change repo location and update references
- move firmwares into `/firmware`-subdir
- update deps and tooling

# v0.5.2

- add revised nRF-FRAM Target v1.3e (no functional changes)
- update GPI, which now supports this target
- adapt trafficbench / rf-survey and generate link-matrix
- deprecate old design-files (prior v1.3)
- update deps and tooling

# v0.5.1

- add documentation
- update deps
- fix QA

# v0.5.0

- adapt firmware to nRF-FRAM Target v1.3
- improve testing
- add new hardware
  - target v1.3, manufactured and tested
  - target v1.2 (skipped)
  - target adapter
  - debug adapter
  - target cage
- update & adapt documentation
- tooling
  - add templates for issues (bug, feature)
  - add dependabot-updater
- update deps
- add code of conduct

# v0.4.3

- last version to support nRF-FRAM Targets v1.1 & v1.0

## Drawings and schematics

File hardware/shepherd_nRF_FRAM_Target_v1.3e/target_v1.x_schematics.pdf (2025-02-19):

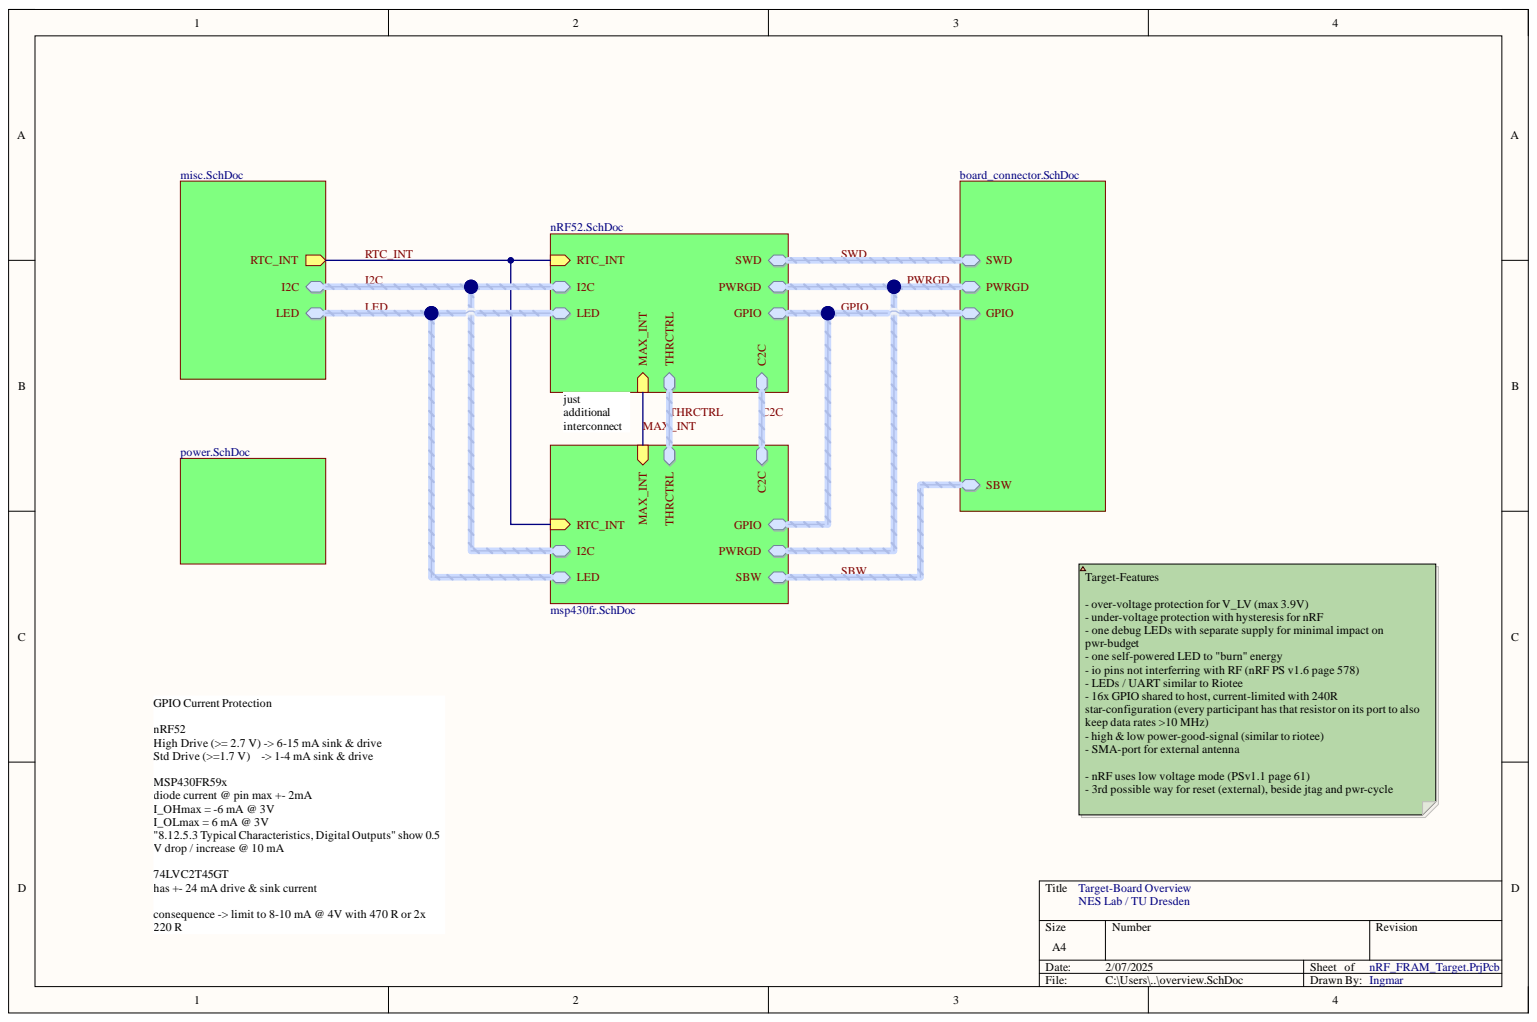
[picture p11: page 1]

- over-voltage protection for V_LV (max 3.9V)
- under-voltage protection with hysteresis for nRF
- one debug LEDs with separate supply for minimal impact on
pwr-budget
- one self-powered LED to "burn" energy
- io pins not interferring with RF (nRF PS v1.6 page 578)
- LEDs / UART similar to Riotee
- 16x GPIO shared to host, current-limited with 240R
star-configuration (every participant has that resistor on its port to also
keep data rates >10 MHz)
- high & low power-good-signal (similar to riotee)
- SMA-port for external antenna

nRF52
High Drive (>= 2.7 V) -> 6-15 mA sink & drive
Std Drive (>=1.7 V) -> 1-4 mA sink & drive

MSP430FR59x
diode current @ pin max +- 2mA
I_OHmax = -6 mA @ 3V
I_OLmax = 6 mA @ 3V
"8.12.5.3 Typical Characteristics, Digital Outputs" show 0.5
V drop / increase @ 10 mA

- nRF uses low voltage mode (PSv1.1 page 61)
- 3rd possible way for reset (external), beside jtag and pwr-cycle

74LVC2T45GT
has +- 24 mA drive & sink current

Title
NES Lab / TU Dresden

consequence -> limit to 8-10 mA @ 4V with 470 R or 2x

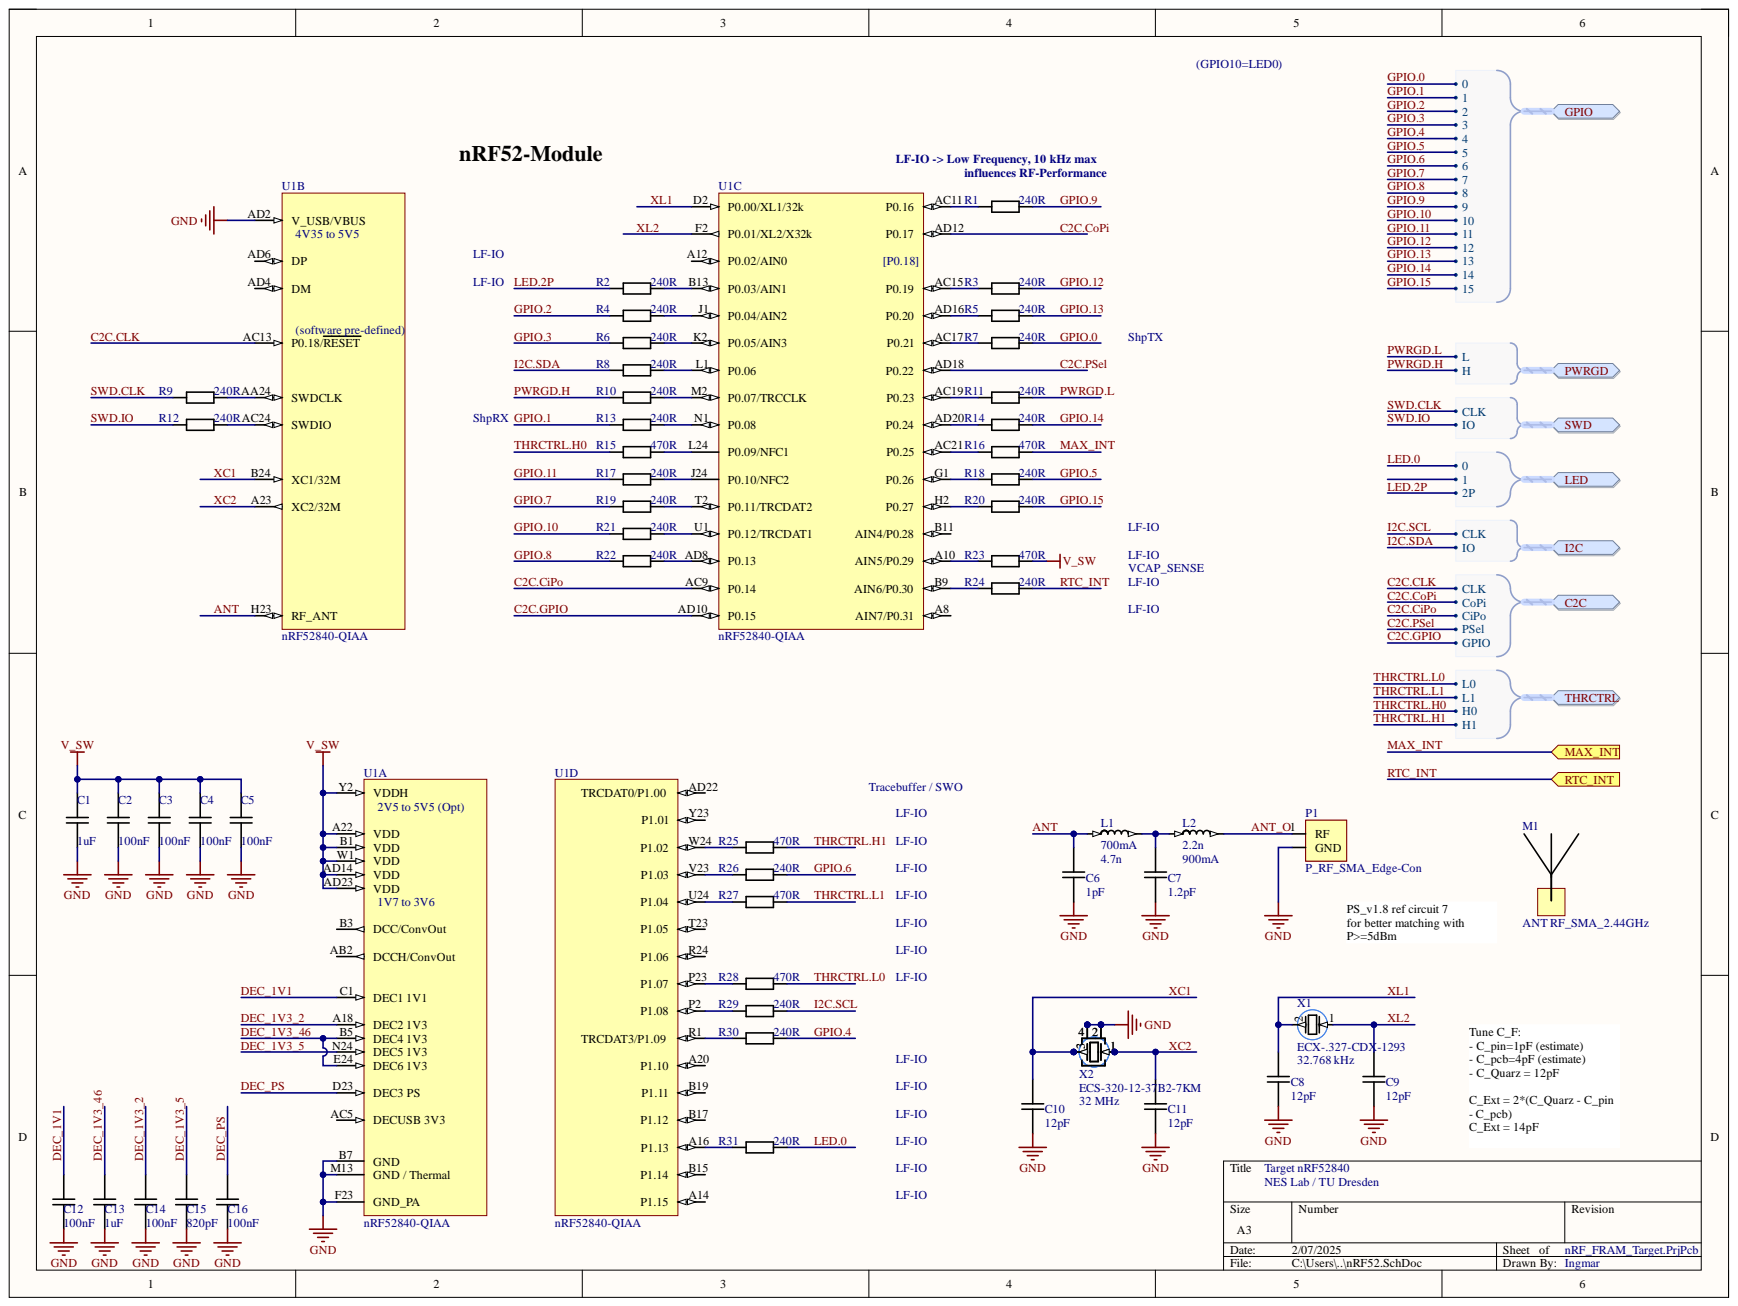
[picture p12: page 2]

LF-IO -> Low Frequency, 10 kHz max

PS_v1.8 ref circuit 7
for better matching with
P>=5dBm

Target nRF52840
NES Lab / TU Dresden

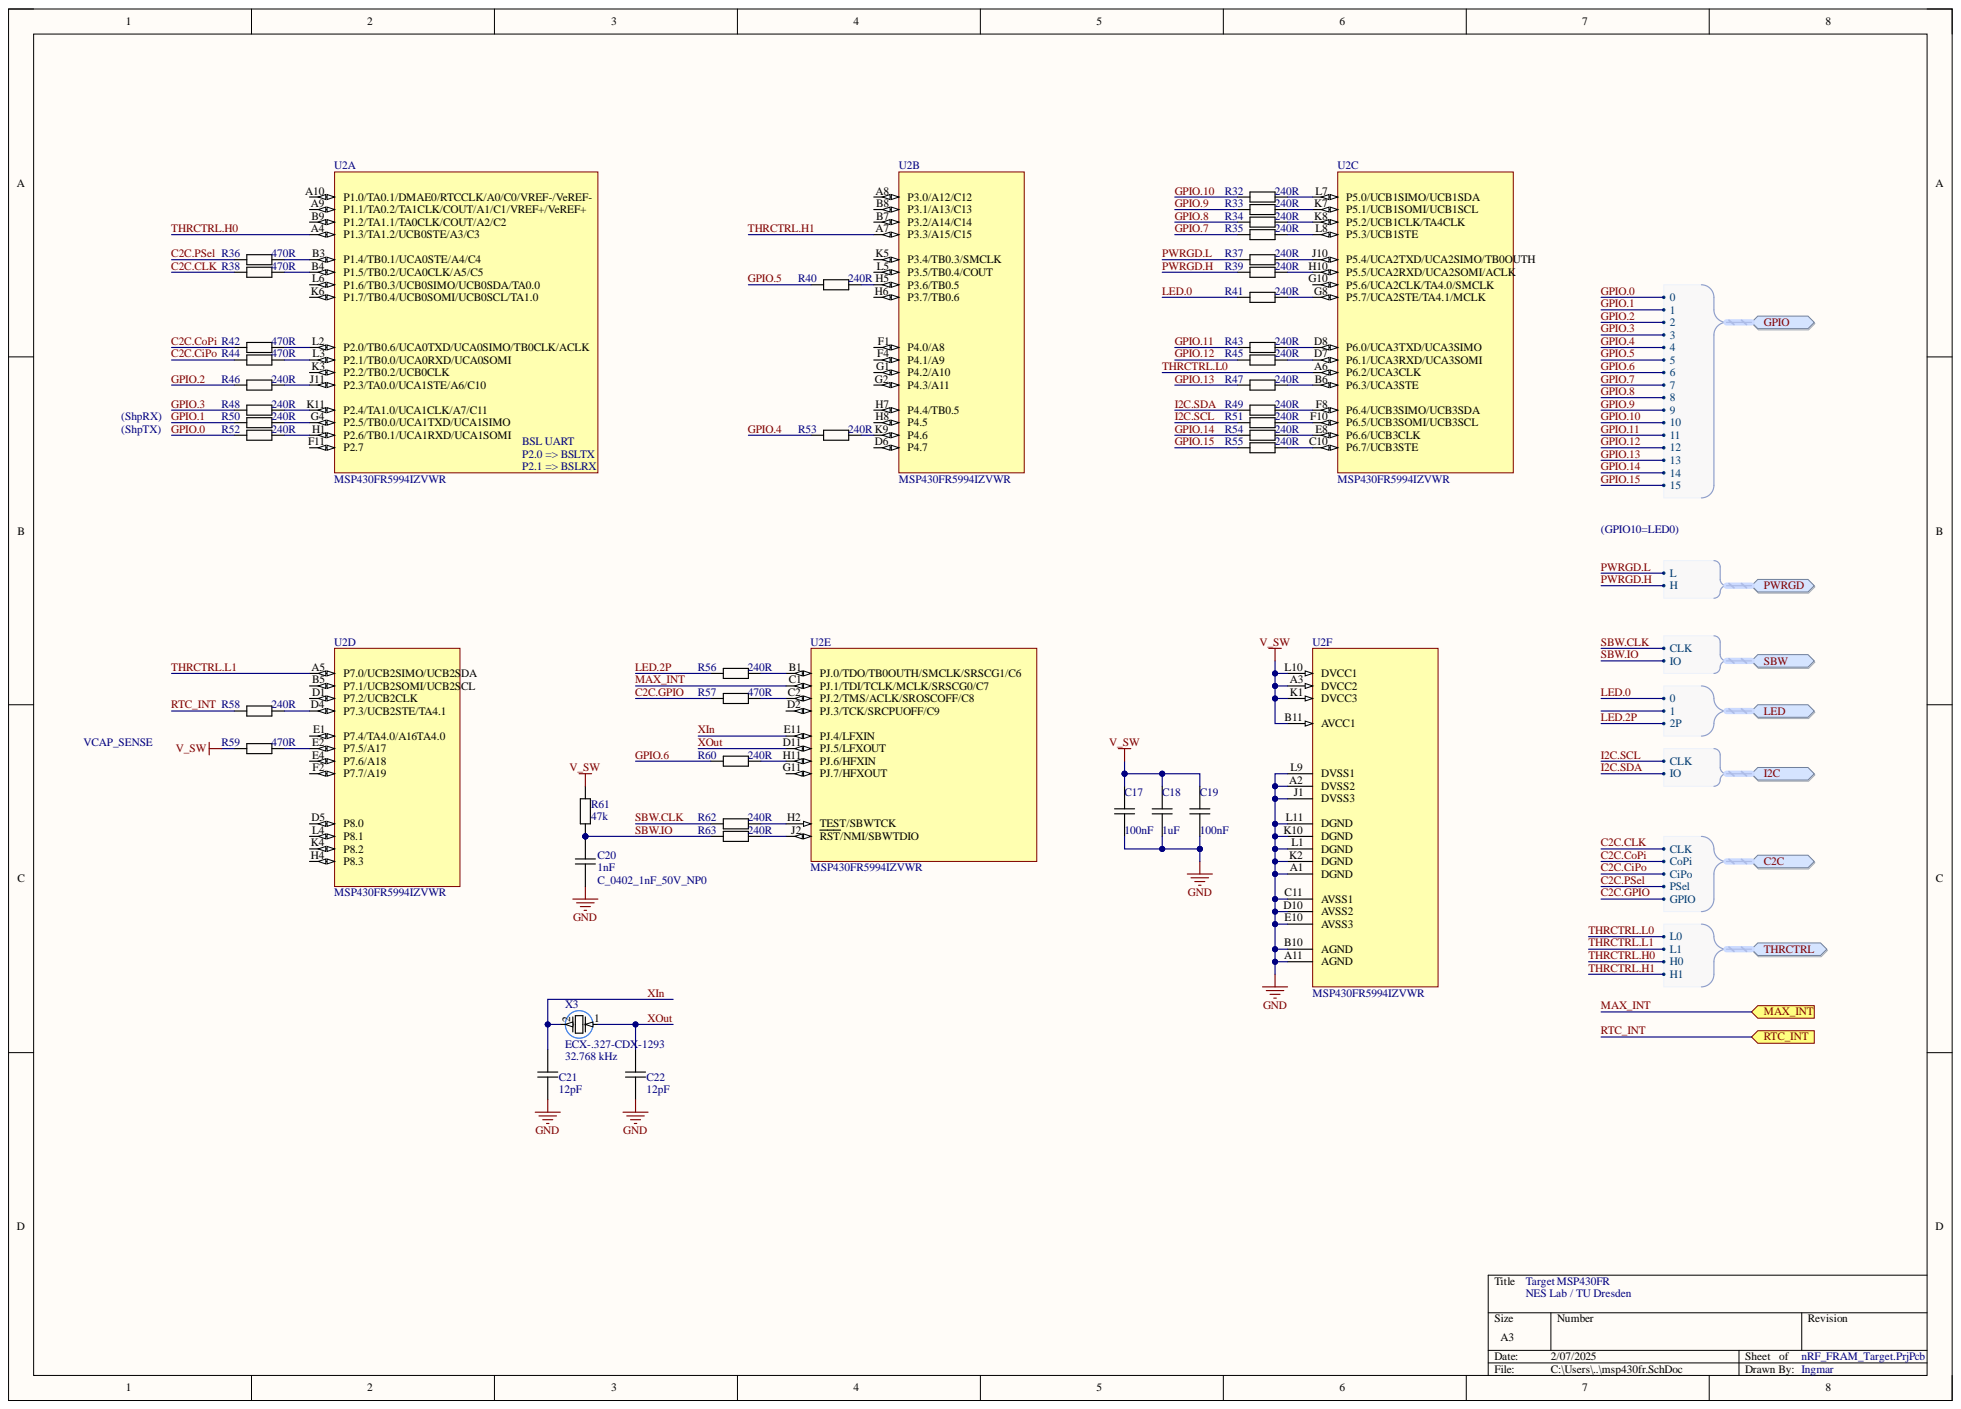
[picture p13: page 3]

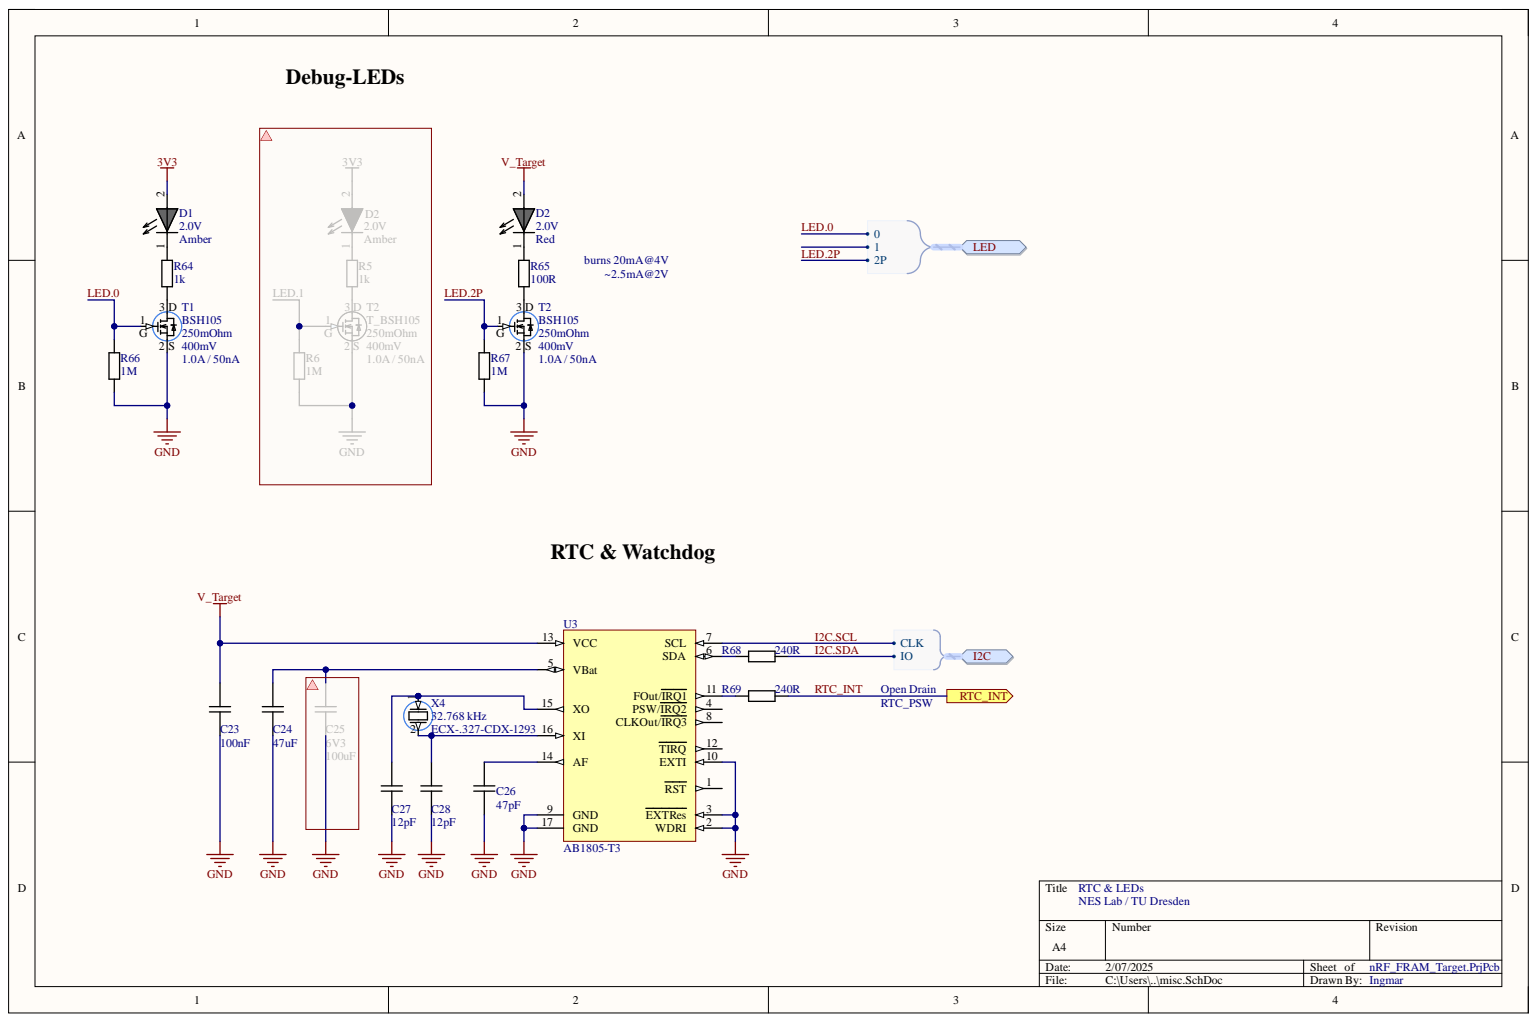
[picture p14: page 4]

GND 17

Title
NES Lab / TU Dresden

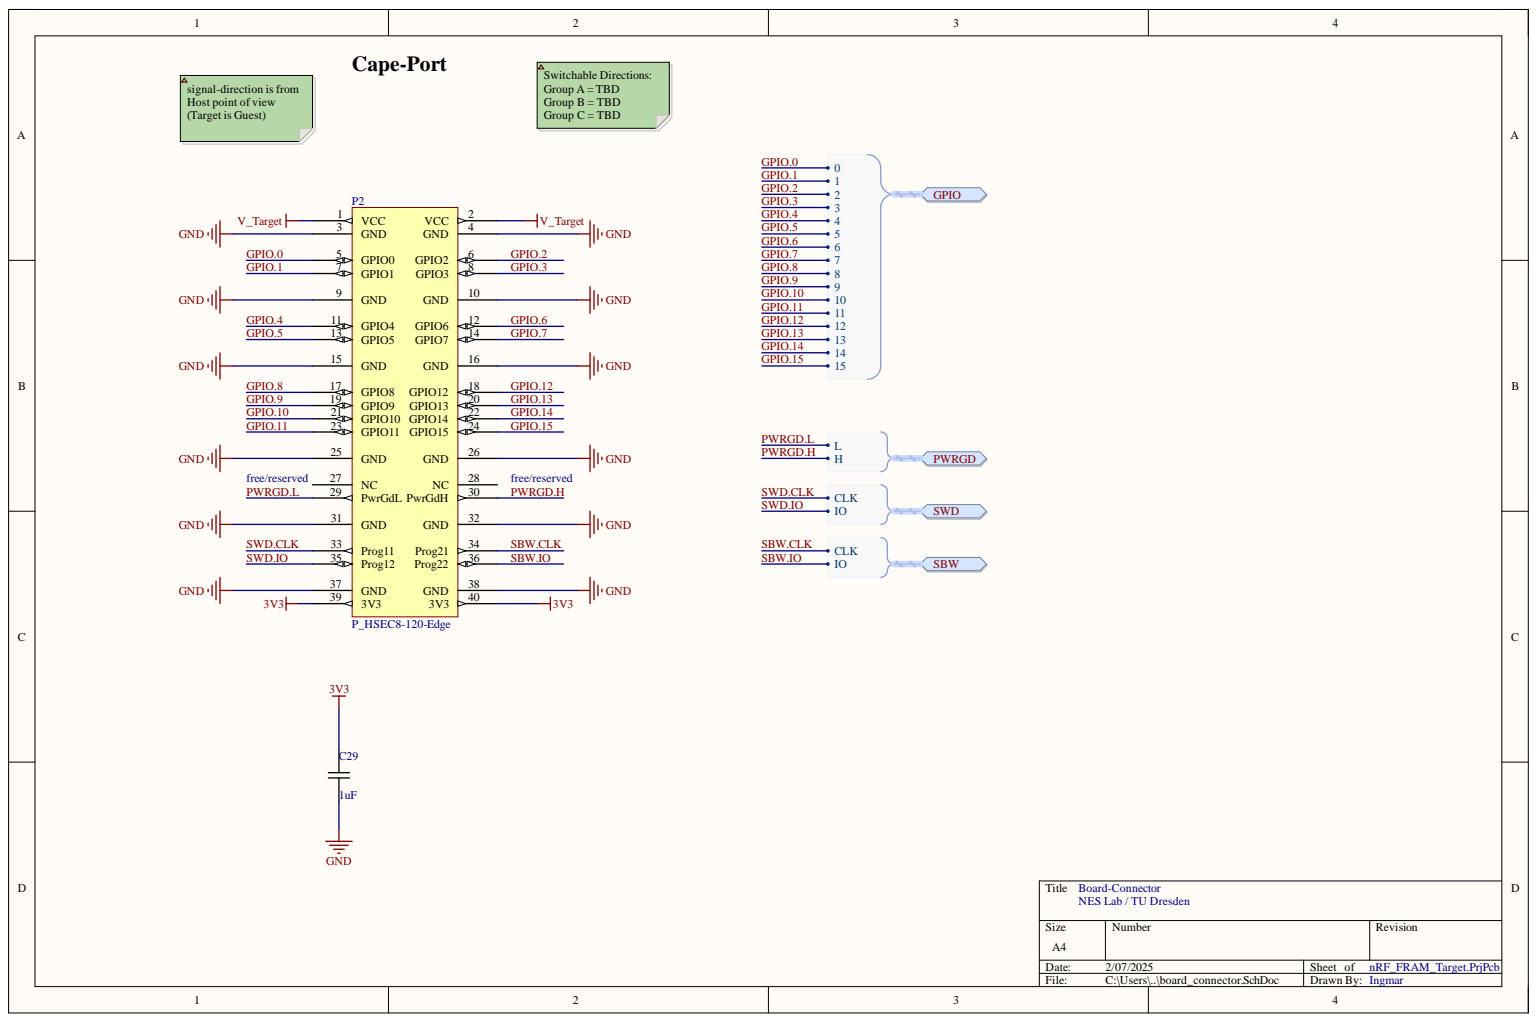
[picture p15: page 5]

GPIO.0 GPIO.1 GPIO.2 GPIO.3 GPIO.4 GPIO.5 GPIO.6

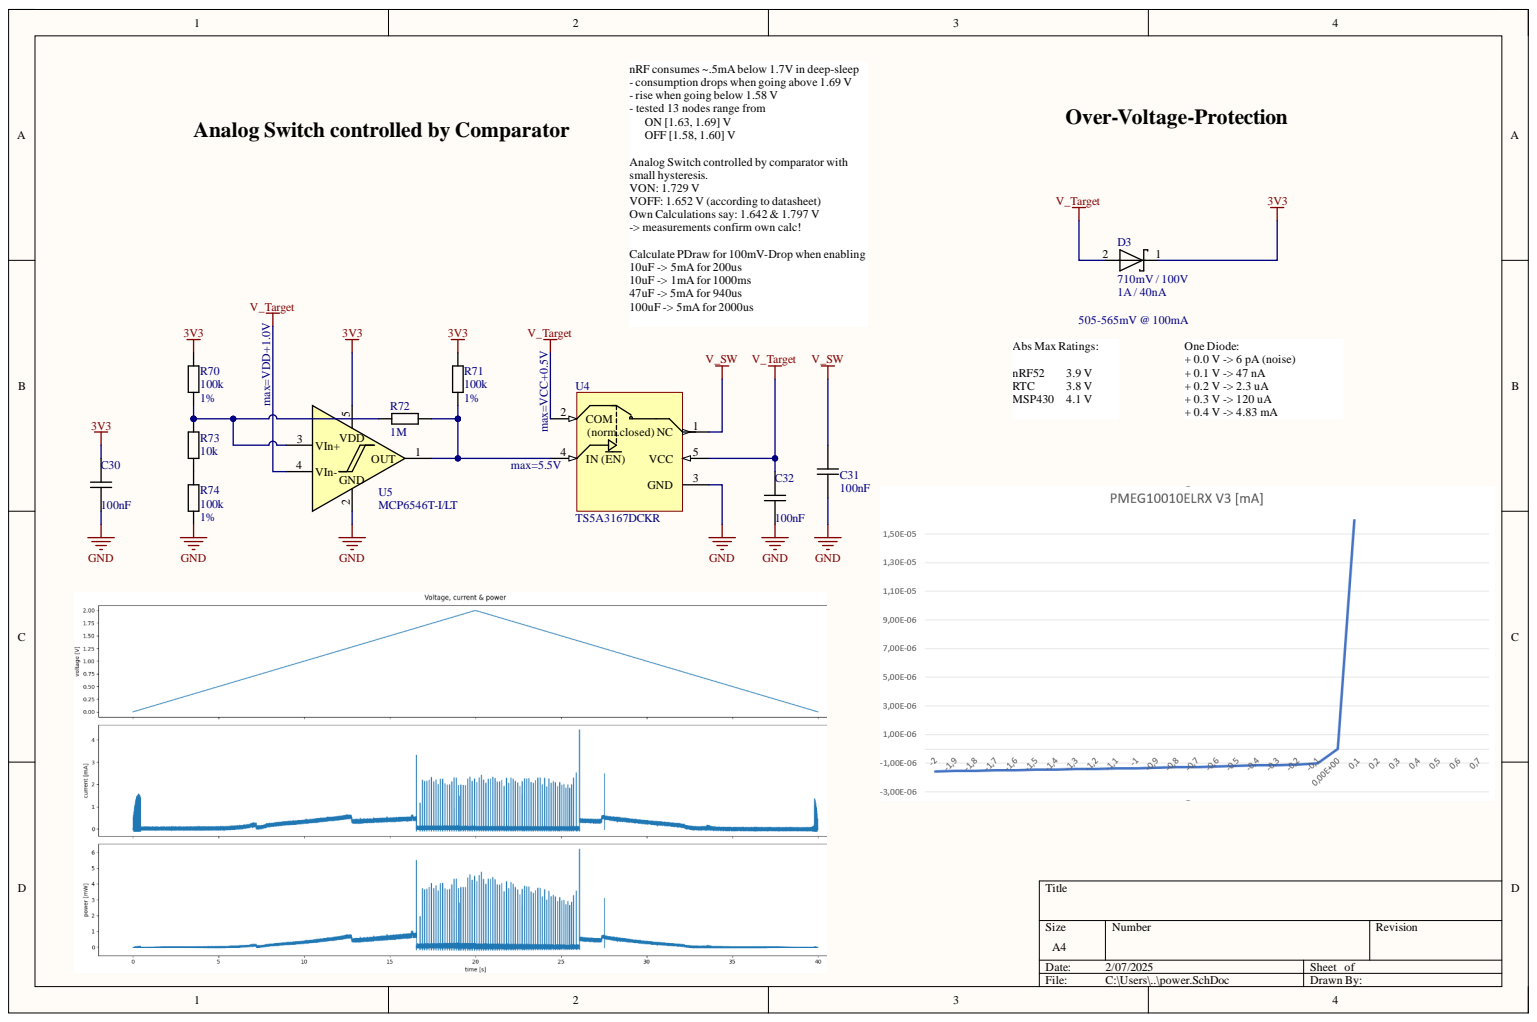
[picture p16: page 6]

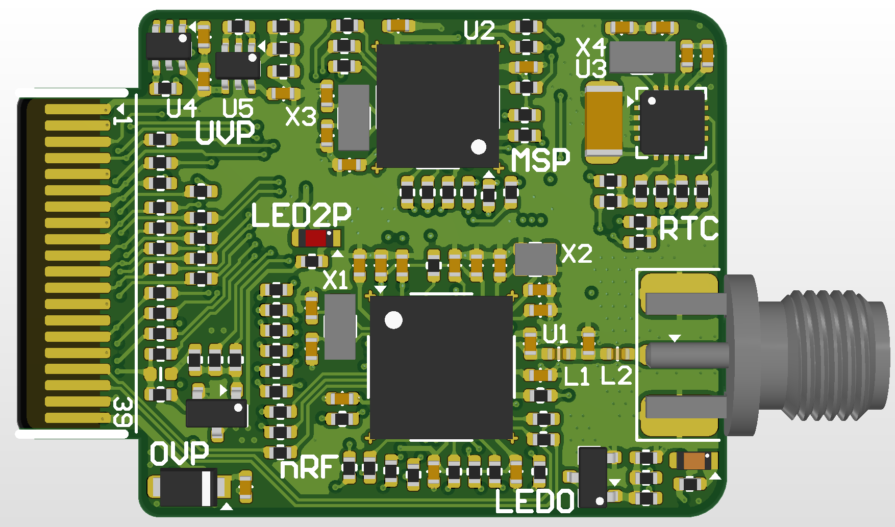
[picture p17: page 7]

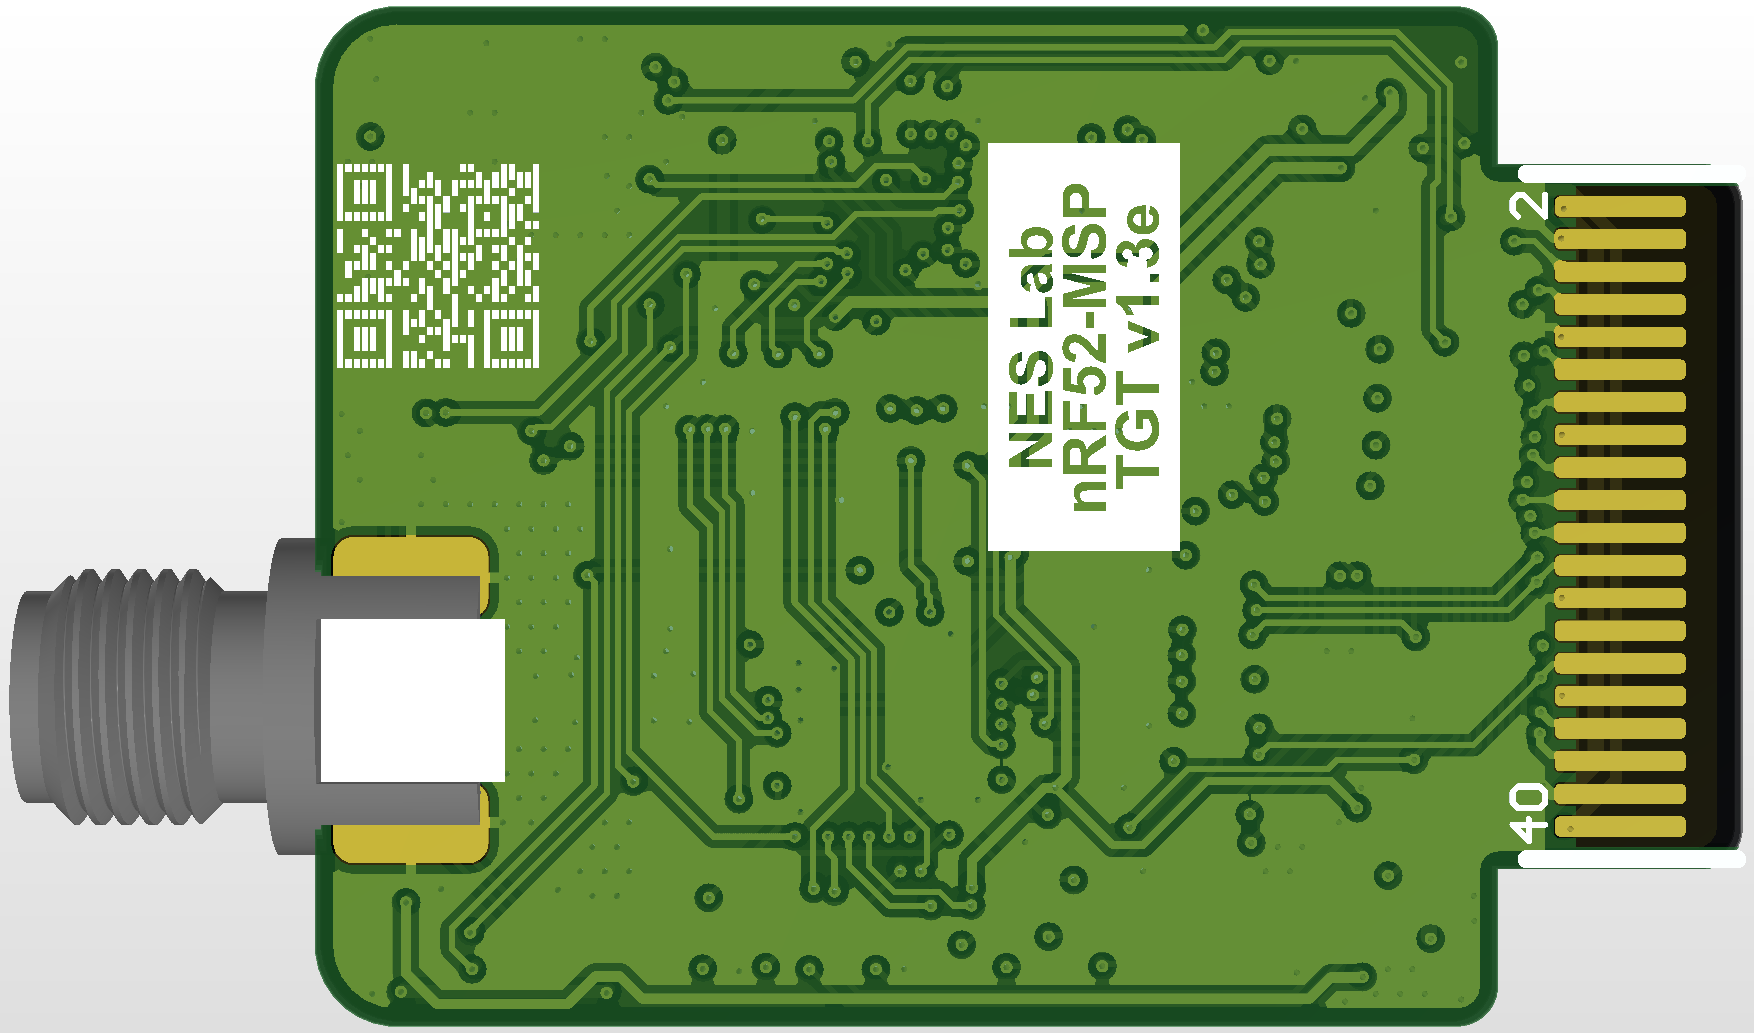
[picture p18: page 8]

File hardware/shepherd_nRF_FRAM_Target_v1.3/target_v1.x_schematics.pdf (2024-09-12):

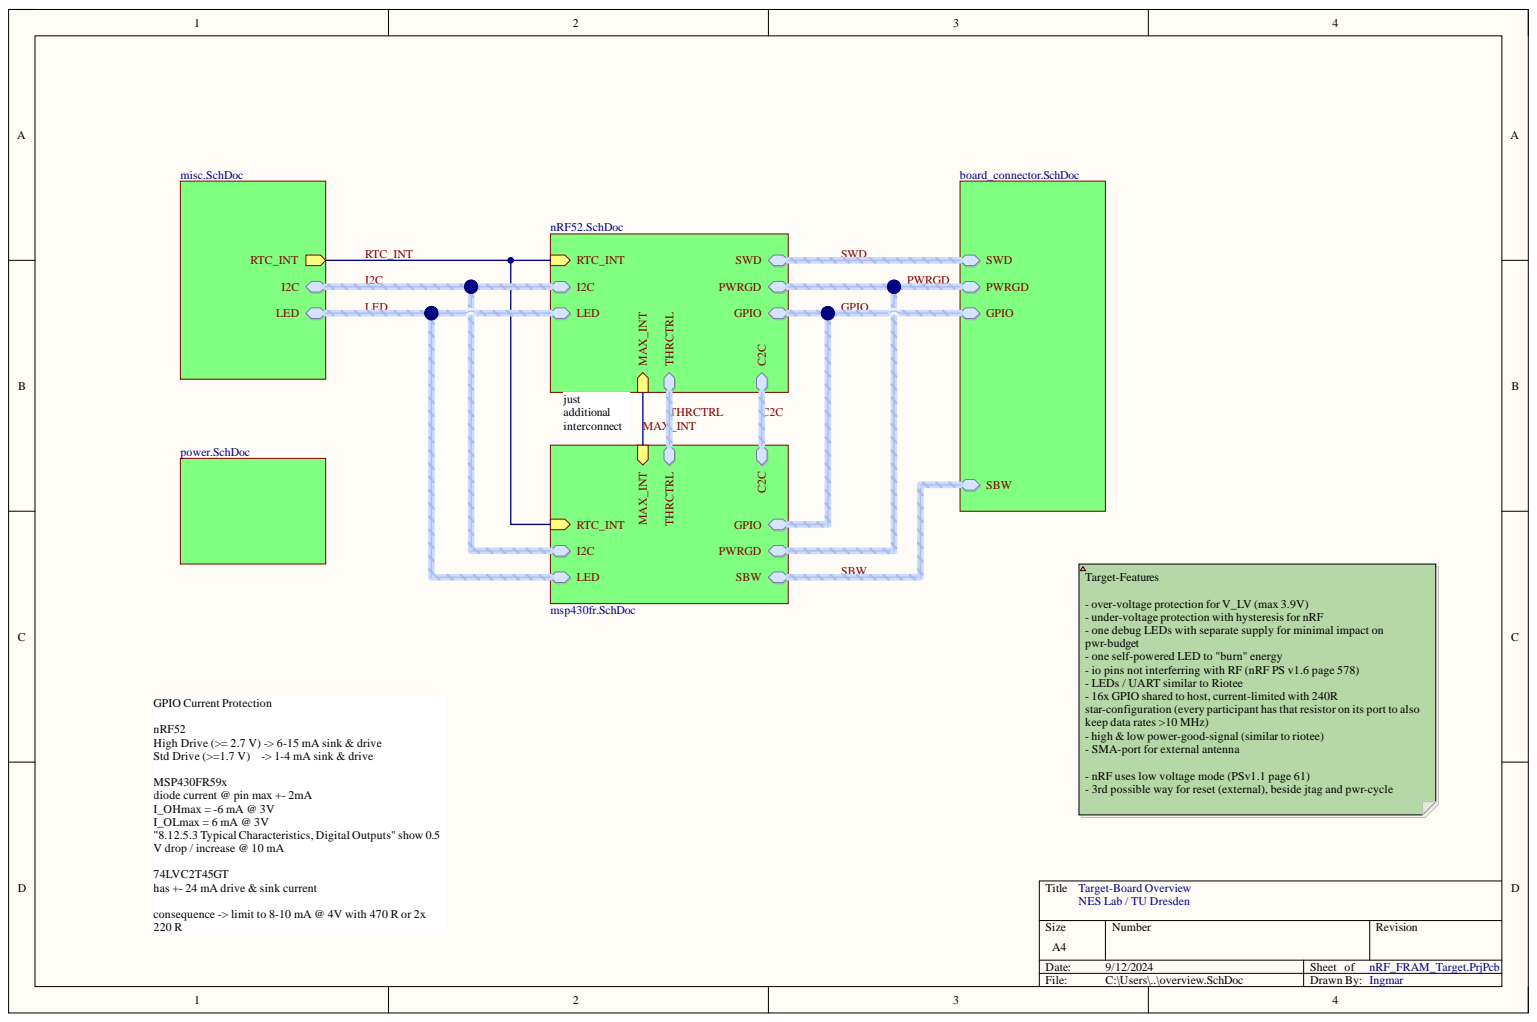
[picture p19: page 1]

- over-voltage protection for V_LV (max 3.9V)
- under-voltage protection with hysteresis for nRF
- one debug LEDs with separate supply for minimal impact on
pwr-budget
- one self-powered LED to "burn" energy
- io pins not interferring with RF (nRF PS v1.6 page 578)
- LEDs / UART similar to Riotee
- 16x GPIO shared to host, current-limited with 240R
star-configuration (every participant has that resistor on its port to also
keep data rates >10 MHz)
- high & low power-good-signal (similar to riotee)
- SMA-port for external antenna

nRF52
High Drive (>= 2.7 V) -> 6-15 mA sink & drive
Std Drive (>=1.7 V) -> 1-4 mA sink & drive

MSP430FR59x
diode current @ pin max +- 2mA
I_OHmax = -6 mA @ 3V
I_OLmax = 6 mA @ 3V
"8.12.5.3 Typical Characteristics, Digital Outputs" show 0.5
V drop / increase @ 10 mA

- nRF uses low voltage mode (PSv1.1 page 61)
- 3rd possible way for reset (external), beside jtag and pwr-cycle

74LVC2T45GT
has +- 24 mA drive & sink current

Title
NES Lab / TU Dresden

consequence -> limit to 8-10 mA @ 4V with 470 R or 2x

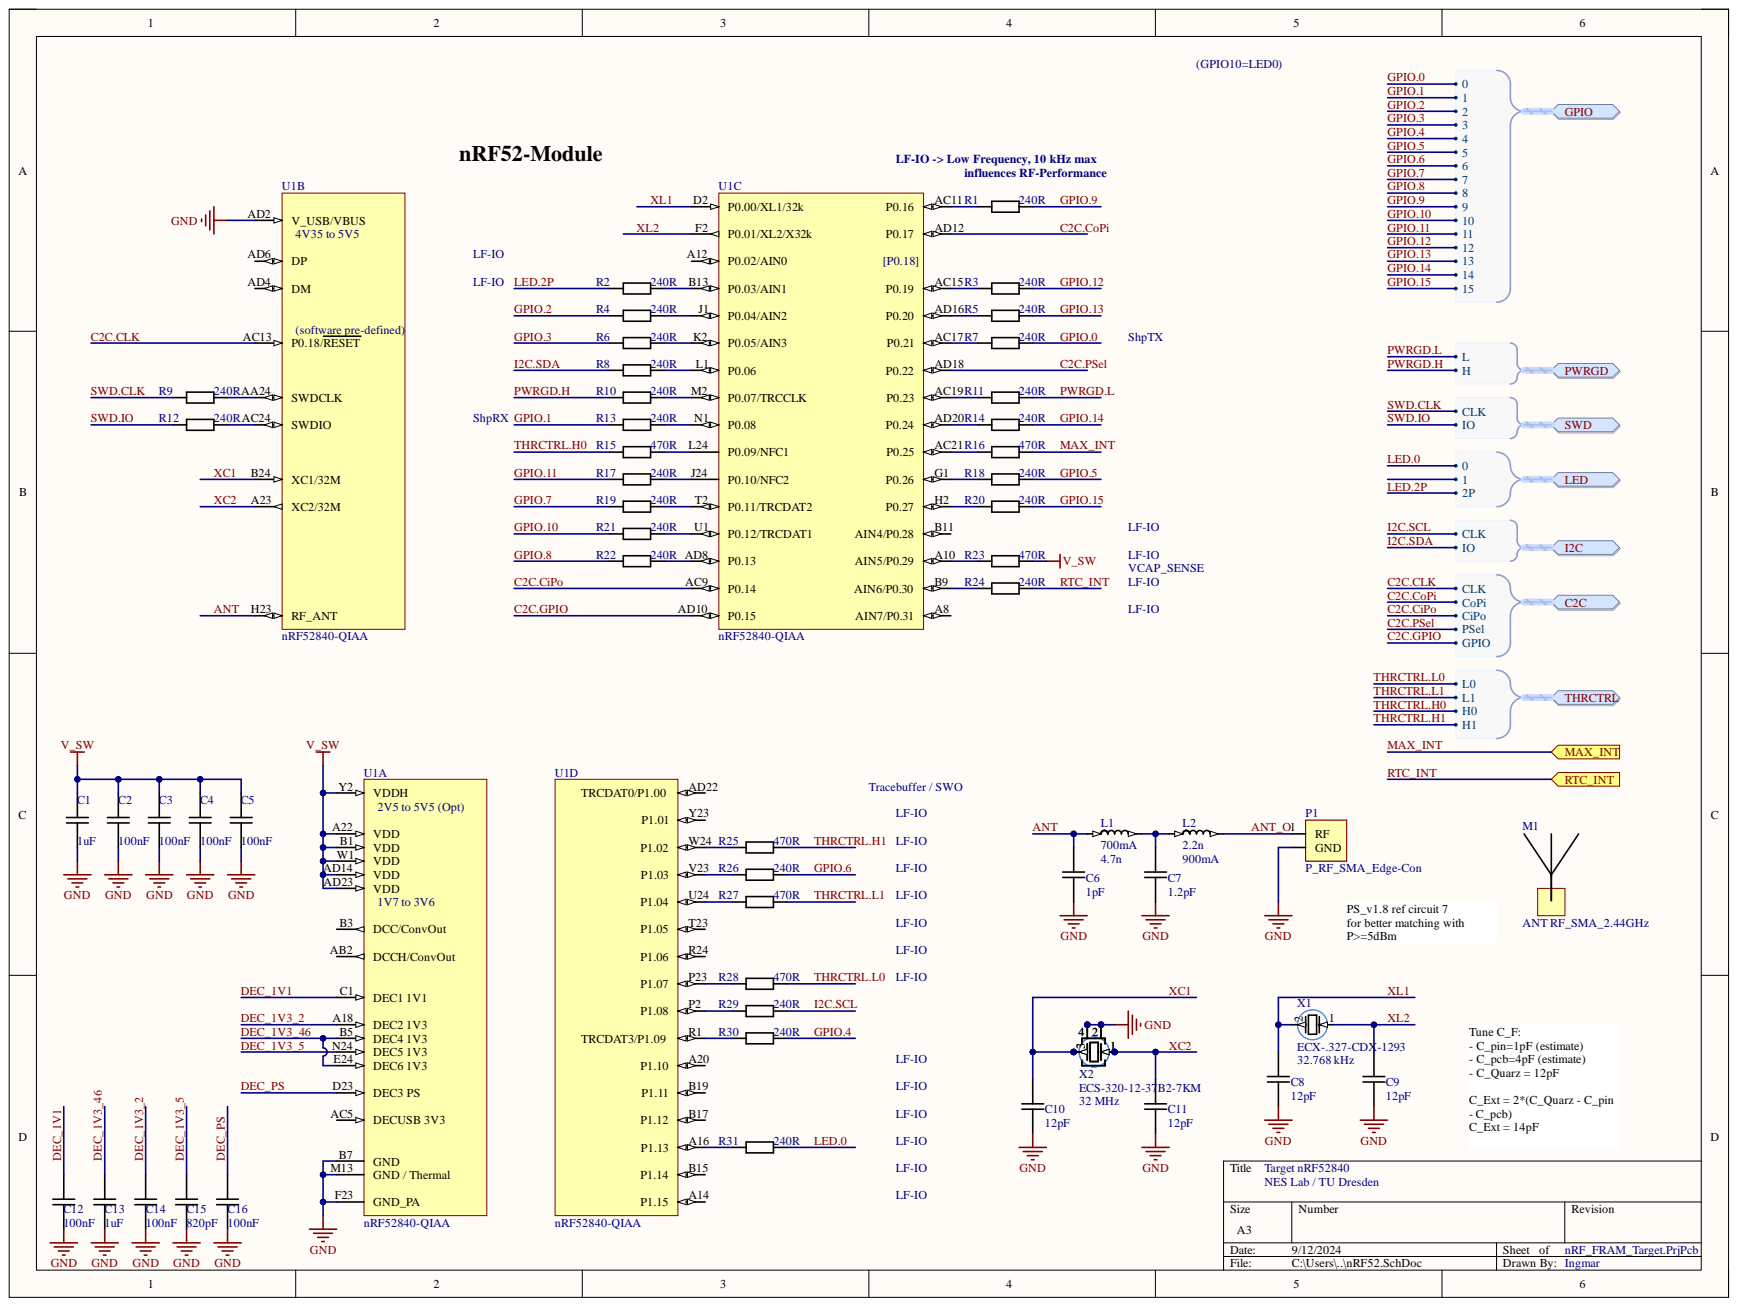
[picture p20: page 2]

LF-IO -> Low Frequency, 10 kHz max

PS_v1.8 ref circuit 7
for better matching with
P>=5dBm

Target nRF52840
NES Lab / TU Dresden

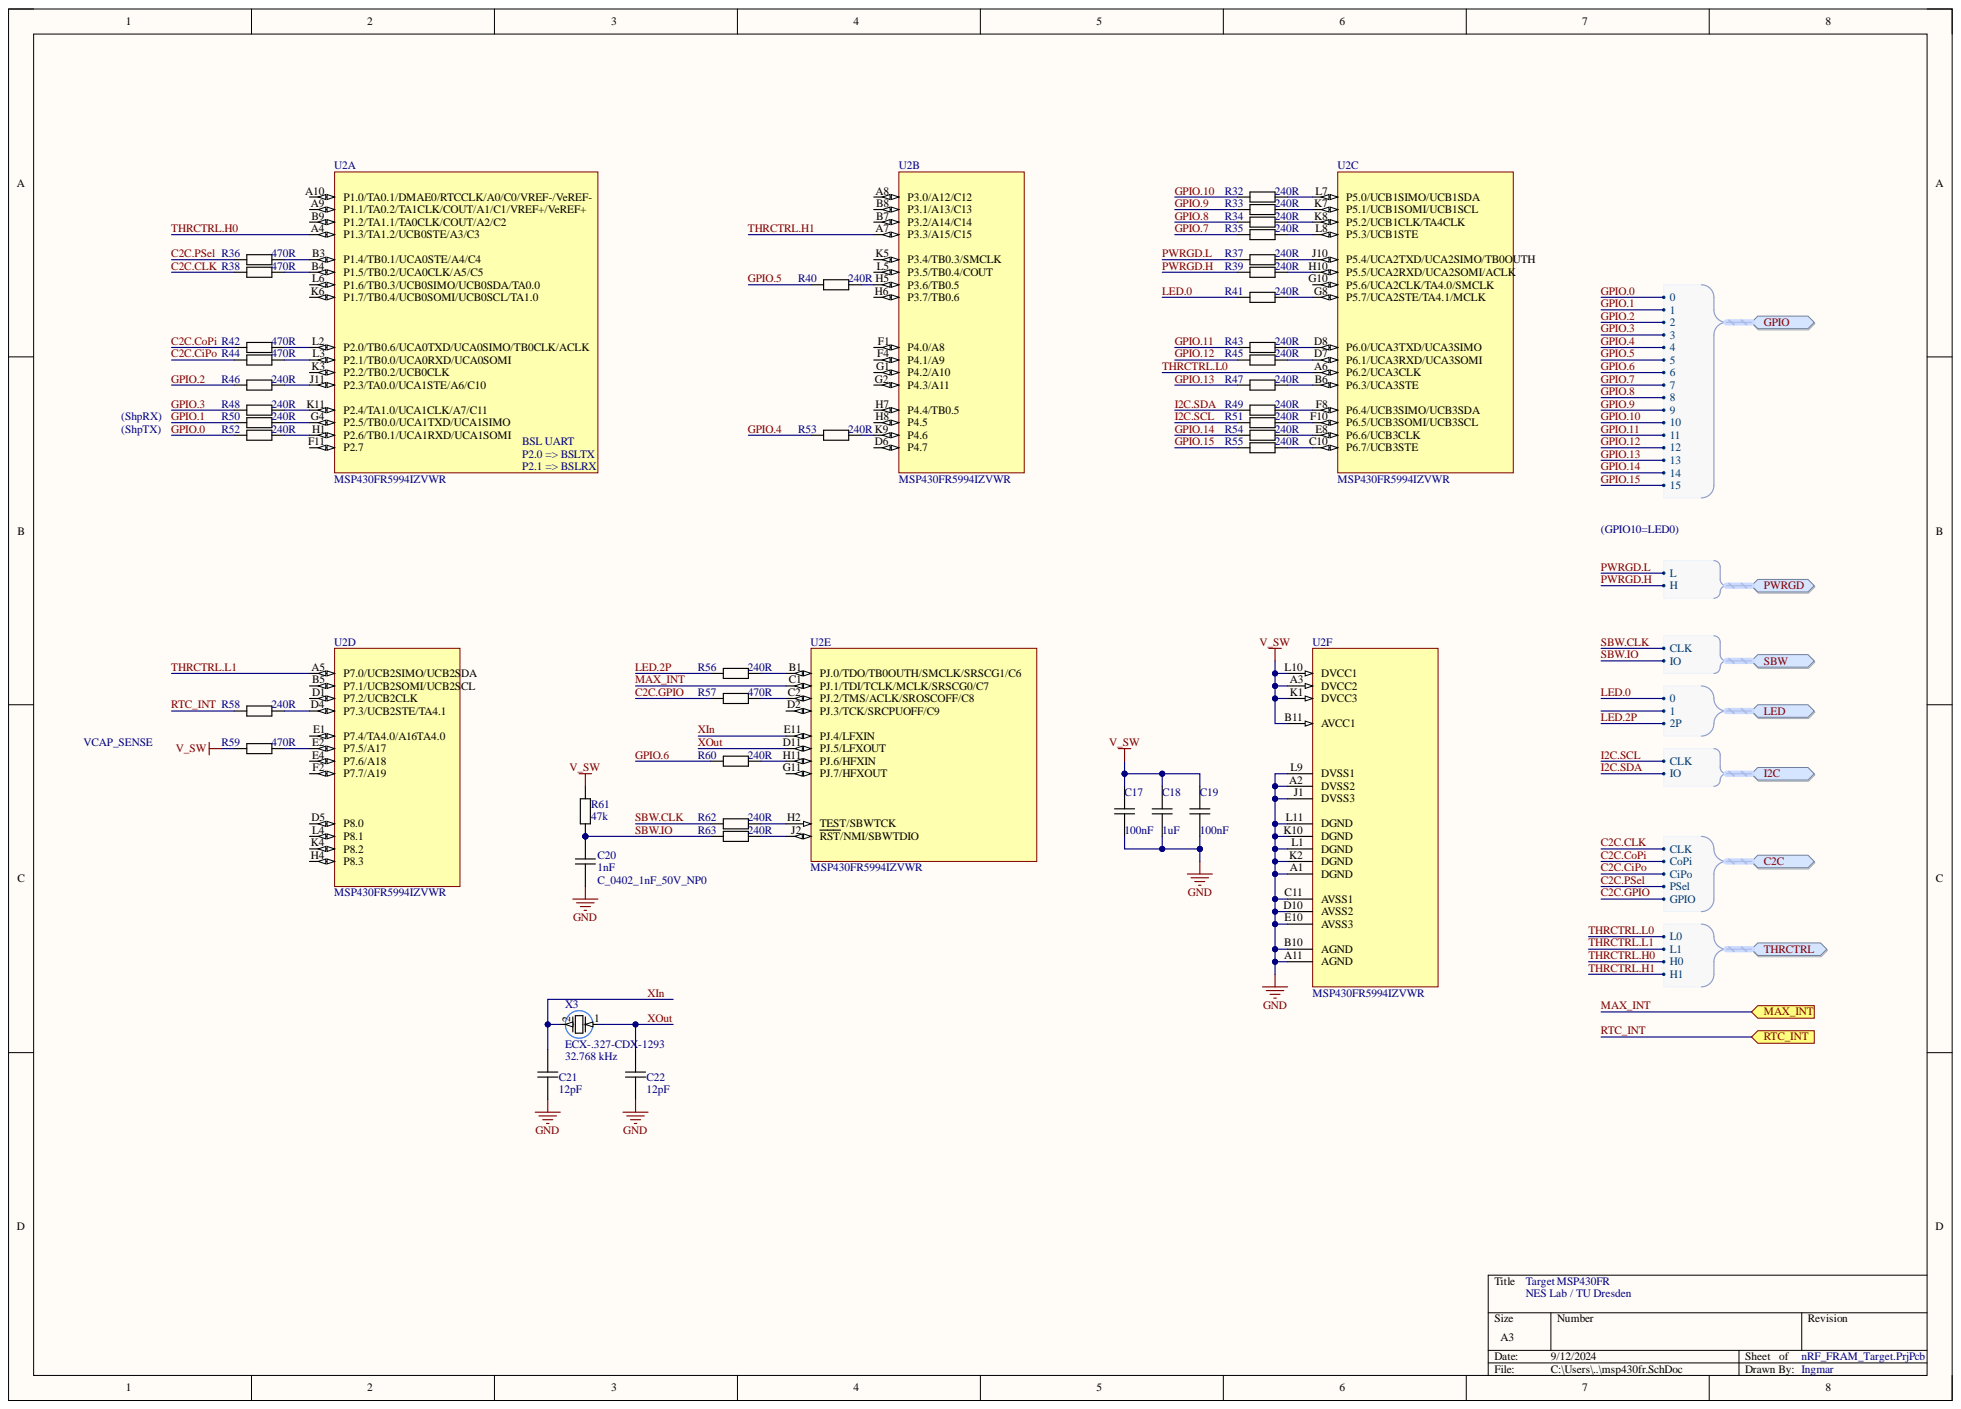
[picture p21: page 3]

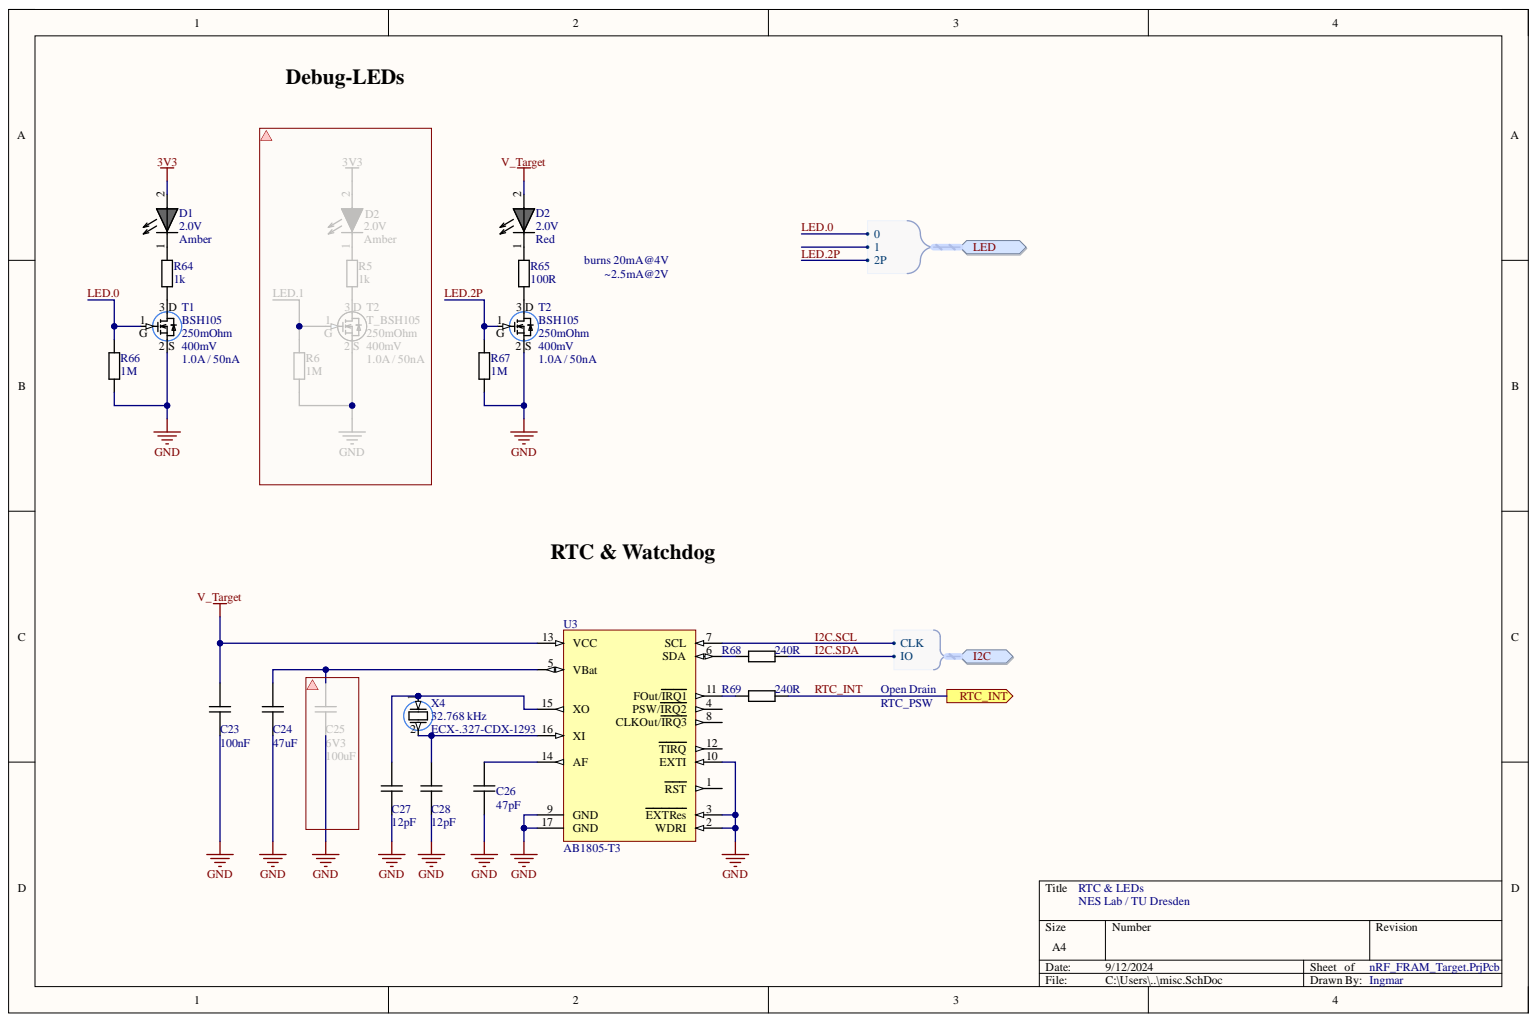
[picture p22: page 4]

GND 17

Title
NES Lab / TU Dresden


GPIO.0 GPIO.1 GPIO.2 GPIO.3 GPIO.4 GPIO.5 GPIO.6







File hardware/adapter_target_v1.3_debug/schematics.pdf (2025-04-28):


signal-direction is from
Host point of view
(Target is Guest)

Title
NES Lab / TU Dresden








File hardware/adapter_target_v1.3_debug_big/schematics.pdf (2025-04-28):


GPIO.0 GPIO.1 GPIO.2 GPIO.3 GPIO.4 GPIO.5 GPIO.6 GPIO.7 GPIO.8 GPIO.9 GPIO.1

GPIO.0 GPIO.2 GPIO.4 GPIO.6

GPIO.1 GPIO.3 GPIO.5 GPIO.7



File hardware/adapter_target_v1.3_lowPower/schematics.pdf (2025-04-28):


signal-direction is from
Host point of view
(Target is Guest)

Allow to disconnect target from
observer as far as possible to
reduce leakage. Programming lines
can be activated via jumpers.

Title
NES Lab / TU Dresden













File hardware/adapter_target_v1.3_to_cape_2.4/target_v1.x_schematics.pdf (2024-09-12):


GPIO.0 GPIO.1 GPIO.2 GPIO.3 GPIO.4 GPIO.5 GPIO.6



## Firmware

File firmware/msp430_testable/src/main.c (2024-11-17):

#include <msp430.h>
#include <msp430fr5994.h>
#include <stdbool.h>
#include <stdint.h>

// see shepherd_node_id.c for details
extern const uint16_t SHEPHERD_NODE_ID;

/*
    MSP430 Pin-Name to int-Conversion:
    - Port J = 0, Port 1-8 stay same
    - Num = 8 * Port + Port.Pin
    - example: P5.5 becomes 8 * 5 + 5 = 45
 */

// Adapted pinout for Target V1.2 (Riotee)
#define PIN_UART_TX (8 * 2 + 5) // P2.5
#define PIN_UART_RX (8 * 2 + 6) // P2.6

#define GPIO0       PIN_UART_RX
#define GPIO1       PIN_UART_TX
#define GPIO2       (8 * 2 + 3) // P2.3
#define GPIO3       (8 * 2 + 4) //   .4
#define GPIO4       (8 * 4 + 6) // P4.6
#define GPIO5       (8 * 3 + 6) // P3.6
#define GPIO6       (8 * 0 + 6) // PJ.6
#define GPIO7       (8 * 5 + 3) // P5.3
#define GPIO8       (8 * 5 + 2) //   .2
#define GPIO9       (8 * 5 + 1) //   .1
#define GPIO10      (8 * 5 + 0) //   .0
#define GPIO11      (8 * 6 + 0) // P6.0
#define GPIO12      (8 * 6 + 1) //   .1
#define GPIO13      (8 * 6 + 3) //   .3
#define GPIO14      (8 * 6 + 6) //   .6
#define GPIO15      (8 * 6 + 7) //   .7
#define PWRGDL      (8 * 5 + 4) // P5.4
#define PWRGDH      (8 * 5 + 5) //   .5

#define PIN_LED0    (8 * 5 + 7) // P5.7 -> powered externally
//#define PIN_LED1    (40) // P5.0 -> powered externally
#define PIN_LED2    (8 * 0 + 0) // PJ.0 -> burns energy-budget

#define I2C_SCL     (8 * 6 + 5) // P6.05
#define I2C_SDA     (8 * 6 + 4)
//#define RTC_INT     (8 * 7 + 3) // output of RTC, not controllable
#define MAX_INT     (8 * 0 + 1) // output of MAX-IC

#define C2C_CLK     (8 * 1 + 5)
#define C2C_CoPi    (8 * 2 + 0)
#define C2C_CiPo    (8 * 2 + 1)
#define C2C_PSel    (8 * 1 + 4)
#define C2C_GPIO    (8 * 0 + 2)

#define THRCTRL_H0  (8 * 1 + 3)
#define THRCTRL_H1  (8 * 3 + 3)
#define THRCTRL_L0  (8 * 6 + 2)
#define THRCTRL_L1  (8 * 7 + 0)

// index with reference to names of shepherds target-port
const uint32_t gpios[] = {GPIO0, GPIO1,  GPIO2,  GPIO3,  GPIO4,  GPIO5,  GPIO6,  GPIO7,  GPIO8,
                          GPIO9, GPIO10, GPIO11, GPIO12, GPIO13, GPIO14, GPIO15, PWRGDL, PWRGDH};
const uint32_t pins[]  = {GPIO0, /*GPIO1,*/ GPIO2, GPIO3,  GPIO4,  GPIO5,  GPIO6,  GPIO7,  GPIO8,
                          GPIO9, GPIO10,           GPIO11, GPIO12, GPIO13, GPIO14, GPIO15, PWRGDL,
                          PWRGDH}; // without uart-tx

const uint32_t leds[]  = {PIN_LED0, PIN_LED2};
const uint32_t i2c[]   = {I2C_SCL, I2C_SDA, /*RTC_INT,*/ MAX_INT};
const uint32_t c2c[]   = {C2C_CLK, C2C_CoPi, C2C_CiPo, C2C_PSel, C2C_GPIO};
const uint32_t thr[]   = {THRCTRL_H0, THRCTRL_H1, THRCTRL_L0, THRCTRL_L1};

const uint32_t all[]   = {
        GPIO0,      /*GPIO1,*/ GPIO2,
        GPIO3,      GPIO4,
        GPIO5,      GPIO6,
        GPIO7,      GPIO8,
        GPIO9,      GPIO10,
        GPIO11,     GPIO12,
        GPIO13,     GPIO14,
        GPIO15,     PWRGDL,
        PWRGDH,     PIN_LED0,
        PIN_LED2,   I2C_SCL,
        I2C_SDA,    /*RTC_INT,*/ MAX_INT,
        C2C_CLK,    C2C_CoPi,
        C2C_CiPo,   C2C_PSel,
        C2C_GPIO,   THRCTRL_H0,
        THRCTRL_H1, THRCTRL_L0,
        THRCTRL_L1,
}; // except uart-tx

#define N_PINS  sizeof(pins) / sizeof(uint32_t)
#define N_GPIOS sizeof(gpios) / sizeof(uint32_t)
#define N_LEDS  sizeof(leds) / sizeof(uint32_t)
#define N_I2C   sizeof(i2c) / sizeof(uint32_t)
#define N_C2C   sizeof(c2c) / sizeof(uint32_t)
#define N_THR   sizeof(thr) / sizeof(uint32_t)
#define N_ALL   sizeof(all) / sizeof(uint32_t)

/* PLATFORM SPECIFIC CODE */

static inline void delay_cycles(const uint32_t cycles)
{
    for (uint32_t i = 0; i < cycles; i++) __no_operation();
}

static inline void delay_ms(const uint32_t time)
{
    /* assumptions:
       - boot with 5MHz / 128 = 39 kHz
       - above loop takes 2 clock-cycles
    */
    const uint32_t cycles = time * 33; // 16000; -> very slow without changes
    delay_cycles(cycles);
}

static void set_gpio_state(const uint32_t pin_num, const bool state)
{
    const uint8_t bank = (pin_num >> 3u) & 0b1111u;
    const uint8_t pin  = (pin_num & 0b111u);
    if (bank > 8u) return;

    if (state)
    {
        if (bank == 0) PJOUT |= 1u << pin;
        if (bank == 1) P1OUT |= 1u << pin;
        if (bank == 2) P2OUT |= 1u << pin;
        if (bank == 3) P3OUT |= 1u << pin;
        if (bank == 4) P4OUT |= 1u << pin;
        if (bank == 5) P5OUT |= 1u << pin;
        if (bank == 6) P6OUT |= 1u << pin;
        if (bank == 7) P7OUT |= 1u << pin;
        if (bank == 8) P8OUT |= 1u << pin;
    }
    else
    {
        if (bank == 0) PJOUT &= ~(1u << pin);
        if (bank == 1) P1OUT &= ~(1u << pin);
        if (bank == 2) P2OUT &= ~(1u << pin);
        if (bank == 3) P3OUT &= ~(1u << pin);
        if (bank == 4) P4OUT &= ~(1u << pin);
        if (bank == 5) P5OUT &= ~(1u << pin);
        if (bank == 6) P6OUT &= ~(1u << pin);
        if (bank == 7) P7OUT &= ~(1u << pin);
        if (bank == 8) P8OUT &= ~(1u << pin);
    }
}

static void set_gpio_dir(const uint32_t pin_num, const bool input)
{
    const uint8_t bank = (pin_num >> 3u) & 0b1111u;
    const uint8_t pin  = (pin_num & 0b111u);
    if (bank > 8u) return;

    if (input)
    {
        if (bank == 0) PJDIR &= ~(1u << pin);
        if (bank == 1) P1DIR &= ~(1u << pin);
        if (bank == 2) P2DIR &= ~(1u << pin);
        if (bank == 3) P3DIR &= ~(1u << pin);
        if (bank == 4) P4DIR &= ~(1u << pin);
        if (bank == 5) P5DIR &= ~(1u << pin);
        if (bank == 6) P6DIR &= ~(1u << pin);
        if (bank == 7) P7DIR &= ~(1u << pin);
        if (bank == 8) P8DIR &= ~(1u << pin);
    }
    else
    {
        if (bank == 0) PJDIR |= 1u << pin;
        if (bank == 1) P1DIR |= 1u << pin;
        if (bank == 2) P2DIR |= 1u << pin;
        if (bank == 3) P3DIR |= 1u << pin;
        if (bank == 4) P4DIR |= 1u << pin;
        if (bank == 5) P5DIR |= 1u << pin;
        if (bank == 6) P6DIR |= 1u << pin;
        if (bank == 7) P7DIR |= 1u << pin;
        if (bank == 8) P8DIR |= 1u << pin;
    }
}

static void set_gpio_out(const uint32_t pin_num, const bool enable)
{
    /* similar to nrf52-code */
    set_gpio_state(pin_num, 0u);
    set_gpio_dir(pin_num, !enable);
}

static void gpio_init(void)
{
    /* set all to neutral state: input */
    PJOUT  = 0u;
    PJDIR  = 0x00;
    PJSEL0 = 0u;
    PJSEL1 = 0u;

    P1OUT  = 0u;
    P1DIR  = 0x00;
    P1SEL0 = 0u;
    P1SEL1 = 0u;

    P2OUT  = 0u;
    P2DIR  = 0x00;
    P2SEL0 = 0u;
    P2SEL1 = 0u;

    P3OUT  = 0u;
    P3DIR  = 0x00;
    P3SEL0 = 0u;
    P3SEL1 = 0u;

    P4OUT  = 0u;
    P4DIR  = 0x00;
    P4SEL0 = 0u;
    P4SEL1 = 0u;

    P5OUT  = 0u;
    P5DIR  = 0x00;
    P5SEL0 = 0u;
    P5SEL1 = 0u;

    P6OUT  = 0u;
    P6DIR  = 0x00;
    P6SEL0 = 0u;
    P6SEL1 = 0u;

    P7OUT  = 0u;
    P7DIR  = 0x00;
    P7SEL0 = 0u;
    P7SEL1 = 0u;

    P8OUT  = 0u;
    P8DIR  = 0x00;
    P8SEL0 = 0u;
    P8SEL1 = 0u;
}

/* GENERALIZED GPIO FUNCTIONS */

static void toggle_gpio_one_high(const uint32_t array[], const uint32_t array_size)
{
    /* set array to output */
    for (uint8_t count = 0; count < array_size; count++) { set_gpio_out(array[count], true); }
    delay_ms(100);
    /* switch each pin on in array */
    for (uint8_t count = 0; count < array_size; count++)
    {
        set_gpio_state(array[count], true);
        delay_ms(100);
        set_gpio_state(array[count], false);
    }
    /* set pins to INPUT */
    delay_ms(100);
    for (uint8_t count = 0; count < array_size; count++) { set_gpio_out(array[count], false); }
}

/* PRIMARY ROUTINE */


int main(void)
{
    /* Stop watchdog */
    WDTCTL = WDTPW | WDTHOLD | WDTCNTCL;

    /* Apply the GPIO configuration */
    PM5CTL0 &= ~LOCKLPM5;

    /* TEST-CODE, mode: this MCU toggles, the other supervises & reports */
    gpio_init();
    delay_ms(2000);

    /* Switch on GPIO for 100ms in a row */
    toggle_gpio_one_high(leds, N_LEDS);
    delay_ms(2000);

    /* run through all GPIO - to present them to the supervisor */
    toggle_gpio_one_high(all, N_ALL);
    delay_ms(2000);

    /* Switch on LEDs for 100ms in a row (>=8 Reps, depending on node-id) */
    uint32_t rep_sum = SHEPHERD_NODE_ID ? SHEPHERD_NODE_ID >= 8 : 8;
    for (uint32_t reps = 0; reps < rep_sum; reps++) { toggle_gpio_one_high(leds, N_LEDS); }

    /* END OF TEST-CODE */

    /* Disable SVS */
    PMMCTL0_H = PMMPW_H; // PMM Password
    PMMCTL0_L &= ~SVSHE;

    /* turn off the PMM to allow for LPM4.5 */
    PMMCTL0_L |= PMMREGOFF; // set Flag to enter LPM4.5 with LPM4 request

    /* Wait in LPM4 until CS is high */
    __bis_SR_register(GIE + LPM4_bits);
}

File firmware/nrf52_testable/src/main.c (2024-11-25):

#include "nrf52840.h"
#include "nrf52840_bitfields.h"
#include "nrf_delay.h"
#include "nrf_gpio.h"
#include "nrf_gpiote.h"

#include "peripherals.h"
#include "printf.h"

#include "pt.h"

// see shepherd_node_id.c for details
extern const uint16_t SHEPHERD_NODE_ID;

// Adapted pinout for Target V1.2 (Riotee)
#define PIN_UART_TX (8)  // P0.08
#define PIN_UART_RX (21) // P0.21

#define GPIO0       PIN_UART_RX
#define GPIO1       PIN_UART_TX
#define GPIO2       (4)
#define GPIO3       (5)
#define GPIO4       (32 + 9) // P1.09
#define GPIO5       (26)
#define GPIO6       (32 + 3) // P1.03
#define GPIO7       (11)
#define GPIO8       (13)
#define GPIO9       (16)
#define GPIO10      (12)
#define GPIO11      (10)
#define GPIO12      (19)
#define GPIO13      (20)
#define GPIO14      (24)
#define GPIO15      (27)
#define PWRGDL      (23)
#define PWRGDH      (7)

#define PIN_LED0    (32 + 13) // P1.13 -> powered externally
//#define PIN_LED1    12 // P0.12 -> powered externally
#define PIN_LED2    (3) // P0.03 -> burns energy-budget

#define I2C_SCL     (32 + 8) // P1.08
#define I2C_SDA     (6)
#define RTC_INT     (30) // output of RTC, not controllable
#define MAX_INT     (25)

#define C2C_CLK     (18)
#define C2C_CoPi    (17)
#define C2C_CiPo    (14)
#define C2C_PSel    (22)
#define C2C_GPIO    (15)

#define THRCTRL_H0  (9)
#define THRCTRL_H1  (32 + 2)
#define THRCTRL_L0  (32 + 7)
#define THRCTRL_L1  (32 + 4)

// index with reference to names of shepherds target-port
const uint32_t gpios[] = {GPIO0, GPIO1,  GPIO2,  GPIO3,  GPIO4,  GPIO5,  GPIO6,  GPIO7,  GPIO8,
                          GPIO9, GPIO10, GPIO11, GPIO12, GPIO13, GPIO14, GPIO15, PWRGDL, PWRGDH};
const uint32_t pins[]  = {GPIO0, /*GPIO1,*/ GPIO2, GPIO3,  GPIO4,  GPIO5,  GPIO6,  GPIO7,  GPIO8,
                          GPIO9, GPIO10,           GPIO11, GPIO12, GPIO13, GPIO14, GPIO15, PWRGDL,
                          PWRGDH}; // without uart-tx

const uint32_t leds[]  = {PIN_LED0, PIN_LED2};
const uint32_t i2c[]   = {I2C_SCL, I2C_SDA, /*RTC_INT,*/ MAX_INT};
const uint32_t c2c[]   = {C2C_CLK, C2C_CoPi, C2C_CiPo, C2C_PSel, C2C_GPIO};
const uint32_t thr[]   = {THRCTRL_H0, THRCTRL_H1, THRCTRL_L0, THRCTRL_L1};

const uint32_t all[]   = {
        GPIO0,      /*GPIO1,*/ GPIO2,
        GPIO3,      GPIO4,
        GPIO5,      GPIO6,
        GPIO7,      GPIO8,
        GPIO9,      GPIO10,
        GPIO11,     GPIO12,
        GPIO13,     GPIO14,
        GPIO15,     PWRGDL,
        PWRGDH,     PIN_LED0,
        PIN_LED2,   I2C_SCL,
        I2C_SDA,    /*RTC_INT,*/ MAX_INT,
        C2C_CLK,    C2C_CoPi,
        C2C_CiPo,   C2C_PSel,
        C2C_GPIO,   THRCTRL_H0,
        THRCTRL_H1, THRCTRL_L0,
        THRCTRL_L1,
};

#define N_PINS  sizeof(pins) / sizeof(uint32_t)
#define N_GPIOS sizeof(gpios) / sizeof(uint32_t)
#define N_LEDS  sizeof(leds) / sizeof(uint32_t)
#define N_I2C   sizeof(i2c) / sizeof(uint32_t)
#define N_C2C   sizeof(c2c) / sizeof(uint32_t)
#define N_THR   sizeof(thr) / sizeof(uint32_t)
#define N_ALL   sizeof(all) / sizeof(uint32_t)

/* Processes rising GPIO edges */
void gpio_consumer(struct pt *pt)
{
    /* works for up to 8 pins */
    pt_begin(pt);

    const char *slot_num;

    gpiote_init(pins, N_PINS);

    while (1)
    {
        pt_wait(pt, !pt_queue_empty(&q_pin_edges));
        slot_num = pt_queue_pop(&q_pin_edges);
        printf("%c triggered\r\n", *slot_num);
    }

    pt_end(pt);
}

/* Processes commands from UART */
void cmd_consumer(struct pt *pt)
{
    pt_begin(pt);

    static unsigned int pin_idx;

    while (1)
    {
        pt_wait(pt, !pt_queue_empty(&q_cmds));
        const char *cmd = pt_queue_pop(&q_cmds);

        /* Convert ascii number to pin number */
        pin_idx         = *cmd - 0x30;
        if (pin_idx >= N_PINS)
            printf("%c is outside of range of supported pins (%zu)\r\n", *cmd, N_PINS);

        /* Switch on pin for 100us */
        timer_reset();
        nrf_gpiote_event_disable(pin_idx);
        nrf_gpio_cfg_output(pins[pin_idx]);
        nrf_gpio_pin_set(pins[pin_idx]);
        while (timer_now_us() < 100) { pt_yield(pt); }
        nrf_gpio_pin_clear(pins[pin_idx]);
        nrf_gpio_cfg_input(pins[pin_idx], NRF_GPIO_PIN_NOPULL);
        nrf_gpiote_event_enable(pin_idx);
    }

    pt_end(pt);
}

/* PLATFORM SPECIFIC CODE */

static inline void delay_ms(const uint32_t duration)
{
    timer_reset();
    const uint32_t duration_us = duration * 1000;
    while (timer_now_us() < duration_us);
}

static void set_gpio_out(const uint8_t pin_num, const bool enable)
{
    const bool    is_p0 = pin_num < 32;
    const uint8_t pin   = pin_num & 0b11111;

    if (enable)
    {
        nrf_gpio_cfg_output(pin_num);
        nrf_gpio_pin_set(pin_num);
        if (is_p0) NRF_P0->OUTCLR = (1u << pin);
        else NRF_P1->OUTCLR = (1u << pin);
    }
    else
    {
        nrf_gpio_pin_clear(pin_num);
        nrf_gpio_cfg_input(pin_num, NRF_GPIO_PIN_NOPULL);
    }
}

static void set_gpio_state(const uint8_t pin_num, const bool state)
{
    if (state) NRF_P0->OUTSET = (1u << pin_num);
    else NRF_P0->OUTCLR = (1u << pin_num);
}

static bool get_gpio(const uint8_t pin_num)
{
    const bool    is_p0 = pin_num < 32;
    const uint8_t pin   = pin_num & 0b11111;
    uint32_t      value;
    if (is_p0) value = NRF_P0->IN;
    else value = NRF_P1->IN;
    return (value & (1u << pin)) > 0;
}

/* GENERALIZED GPIO FUNCTIONS */

static void toggle_gpio_one_high(const uint32_t array[], const uint8_t array_size)
{
    /* set array to output */
    for (uint8_t count = 0; count < array_size; count++) { set_gpio_out(array[count], true); }
    /* switch each pin on in array */
    for (uint8_t count = 0; count < array_size; count++)
    {
        set_gpio_state(array[count], true);
        delay_ms(100);
        set_gpio_state(array[count], false);
    }
    /* set pins to INPUT */
    for (uint8_t count = 0; count < array_size; count++) { set_gpio_out(array[count], false); }
}

static uint8_t gpio_watcher(const uint32_t array[], const uint8_t array_size)
{
    for (uint8_t count = 0; count < array_size; count++)
    {
        if (get_gpio(array[count])) return count;
    }
    return 0xFF;
}

/* PRIMARY ROUTINE */
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

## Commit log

2023-06-07 add current pcb-manufacturing data
    [40 - MouserBom.xls, Bill of Materials-nRF_FRAM_Target.xlsx, target_c_Copper_Signal_1.gbr, target_c_Copper_Signal_2.gbr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]
2023-06-12 revise pin config to avoid leakage
2023-07-07 improve filter_logs.py
2023-07-20 assemble py-package
2023-08-29 doc + rendering of pcb
2023-09-01 rename pcb-dir
    [40 - MouserBom.xls, Bill of Materials-nRF_FRAM_Target.xlsx, target_c_Copper_Signal_1.gbr, target_c_Copper_Signal_2.gbr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]
2023-09-17 document PCBs and add new V1.1
    [Bill of Materials-nRF_FRAM_Target.xlsx, Pick Place for target_1.1a.csv, target_1.1a_Assembly_Notes.gbr, target_1.1a_Bottom_Designator.gbr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]
2023-09-19 activate PD-Resistors during sleep on msp
2023-09-30 raise tx power to 8 dBm
2024-03-28 add target v1.2
    [BOM++.xlsx, Bill of Materials-nRF_FRAM_Target.xlsx, Pick Place for target_1.2.csv, target_1.2_Assembly_Notes.gbr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]
2024-07-12 add known hw-bugs to current target
2024-07-16 more fw-adaptions to current target schematic
2024-09-12 add new target adapters
    [Bill of Materials-target_adapt_header.xlsx, Bill of Materials-target_adapter.xlsx, Pick Place for tgt_adapter_2v1_2v3.csv, Pick Place for tgt_adapter_header.cs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]
2024-09-12 target design files
    [Bill of Materials-assembly.xlsx, Bill of Materials-nRF_FRAM_Target.xlsx, Bill of Materials_calc.xlsx, target_1.3d_panel_Copper_1_Signal_2.gbr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]
2024-09-12 update doc
    [Pick Place for target_1.3d_panel(OnlyPopulate).csv]
2024-09-26 update hw doc
    [Bill of Materials-assembly.xlsx]
2024-11-17 fix LED-pins
2024-11-25 add cage
    [target_v13_cage.scad, target_v13_cage.stl]
2024-11-25 fix types of printed variables
2024-11-29 add SYNC-LED for Riotee
2024-11-29 GPI Mod - copy power-settings from pca10056
2025-02-19 add revised target v1.3e
    [Bill of Materials-nRF_FRAM_Target(OnlyPopulate).xlsx, Pick Place for target_1.3e(OnlyPopulate).csv, target_1.3e_panel_Copper_1_Signal_2.gbr, target_1.3e_panel_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]
2025-03-11 deprecate older design-files
    [40 - MouserBom.xls, BOM++.xlsx, Bill of Materials-nRF_FRAM_Target.xlsx, Pick Place for target_1.1a.csv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]
2025-04-28 add low power adapter
    [Bill of Materials.xlsx, target_adapt_lowPower_Assembly_Notes.gbr, target_adapt_lowPower_Bottom_Designator.gbr, target_adapt_lowPower_Copper_Signal_Bot.gbr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]
2025-04-28 add debug adapter with one large header
    [Bill of Materials.xlsx, tgt_adapter_header_Assembly_Notes.gbr, tgt_adapter_header_Bottom_Designator.gbr, tgt_adapter_header_Copper_Signal_Bot.gbr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]
2025-04-28 update debug adapter
    stay on 2.54 mm grid
    [Bill of Materials-target_adapt_header.xlsx, Pick Place for tgt_adapter_header.csv, tgt_adapter_header_Assembly_Notes.gbr, tgt_adapter_header_Bottom_Designator.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]
